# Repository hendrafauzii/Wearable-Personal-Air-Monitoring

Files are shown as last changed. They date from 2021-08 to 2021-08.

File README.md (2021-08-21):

# Wearable Personal Air Monitoring

## Daftar Isi
 - [Daftar Isi](#Daftar-isi)  
 - [Deskripsi](#Deskripsi) 
 - [Library Depedency](#Library-depedency)
 - [PCB Design](#PCB-Design) 
 - [Bill of Materials](#BOMs) 
 - [Dashboard](#dasboard-pada-platform-iot-xl-axiata-flex-iot)
 - [Galeri](#Galeri)

## Deskripsi
Perangkat ini dirancang pada tahun 2019 yang dibuat menyerupai sebuah jam tangan bagi penderita sinusitis yang sensitif terhadap perubahan udara. Terdapat beberapa sensor yang digunakan diantaranya  sensor BME280 sebagai pengukuran suhu, kelembapan, dan tekanan udara secara real time, dan MAX30105 sebagai sensor tambahan yang berfungsi untuk mengukur detak jantung. Alat ini akan memberikan notifikasi ketika kondisi udara tidak ideal bagi penderita sinusitis.

## Library Depedency
Perangkat ini diprogram menggunakan ArduinoIDE yang berbasis C/C++, dengan memilih ESP32 Dev Module pada bagian board di ArduinoIDE.
Adapun library depedency yang digunakan diantaranya :

**• Adafruit Sensor** https://github.com/adafruit/Adafruit_Sensor

**• BME280** https://downloads.arduino.cc/libraries/github.com/adafruit/Adafruit_BME280_Library-1.1.0.zip

**• MAX3010x** https://github.com/sparkfun/SparkFun_MAX3010x_Sensor_Library

**• SSD1306 Display** https://github.com/ThingPulse/esp8266-oled-ssd1306

**• PubSub Client** https://github.com/knolleary/pubsubclient

**• ArduinoJson v5** https://github.com/bblanchon/ArduinoJson/tree/5.x

## PCB Design
<p align="left"> 
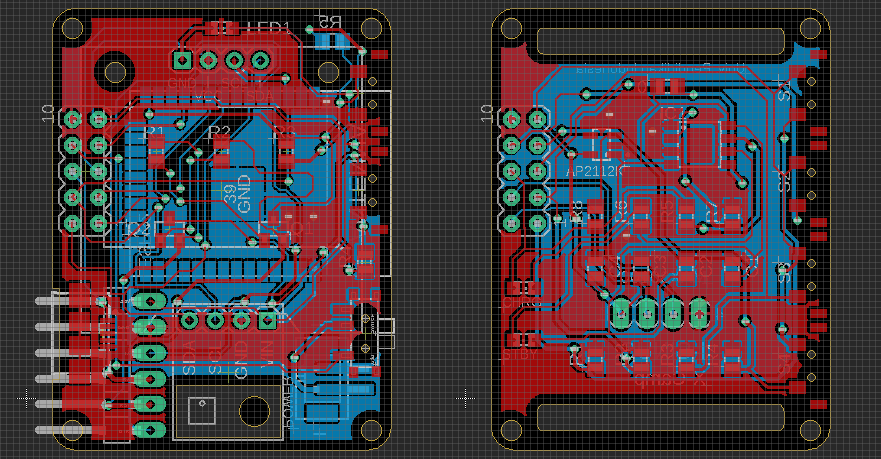
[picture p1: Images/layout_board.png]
  
</p>

## BOMs
**• Bagian Atas**
No | Parts          | Value       | Package                  | Qty 
-- | -------------- | ----------- | ------------------------ | --- |
1  | LED1           | LED         | CHIPLED_0805             |  1  |
2  | SV1	           | MA05        | MA05-2	                  |  1  |
3  | JP1            | PIN HEAD    | 1X06/90                  |  1  |
4  | U$3, U$4       | SIDE SWITCH | SIDE_SWITCH              |  2  |
5  | R1, R2, R4, R5 | 10K	        | R0805                    |  4  |
6  | R3	            | 1K	         | R0805                    |  1  |
7  | U$1	           | BME280	     | BME280                   |	 1  |
8  | OLED-DISPLAY   | OLED-128X64 | 128X64-I2C               |	 1  |
9  | U1	            | ESP32	      | ESP32-WROOM              |  1  |
10 | J1	            | MICRO USB	  | GCT_USB3065-XX-00-A_REVE |  1  |
11 | Q1, Q2	        | MMBT2222A	  | SOT23                    |  2  |
12 | X1	            | POWER       | B2B-PH-SM4-TB            |  1  |
13 | U$2	           | SWITCH	     | MSK-12C02                |  1  |

**• Bagian Bawah**
No | Parts              | Value    | Package          | Qty 
-- | ------------------ | -------- | ---------------- | --- |
1  | CHRG, STBY	        | LED      | CHIPLED_0805     |	 2  |
2  | MAX30100	          | MAX30100 |	MA04-1           |	 1  |
3  | SV1                | MA05-2   |	MA05-2           |	 1  |
4  | 0 (Not Used)       | 0        |	R0805            |	 1  |
5  | R1, R2, R3, R4, R8 | 10K      |	R0805            |	 5  |
6  | C1, C2, C3         | 10uF     |	C0805            |  3  |
7  | R5, R6             | 1K       |	R0805            |  2  |
8  | C4                 | 1uF      |	C0805            |  1  |
9  | R7                 | 2K       |	R0805            |  1  |
10 | U2                 | AP2112K  |	SOT95P285X140-5N |  1  |
11 | S1                 |	BUT1     |	SIDE_SWITCH      |  1  |
12 | S2                 |	BUT2     |	SIDE_SWITCH	     |  1  |
13 | S3                 |	BUT3     |	SIDE_SWITCH	     |  1  |
14 | S4                 |	BUT4     |	SIDE_SWITCH	     |  1  |
15 | IC1                |	TP4056   |	SOP-8	           |  1  |

## Dasboard pada Platform IoT XL Axiata (Flex-IoT)
Perangkat ini dihubungkan dengan Platform IoT XL Axiata [(Flex-IoT)](https://portal.flexiot.xl.co.id/) menggunakan WiFi dengan Protokol MQTT, sehingga dapat dibuat dashboard untuk monitoring seperti yang terlihat pada gambar berikut. 

<p align="left"> 
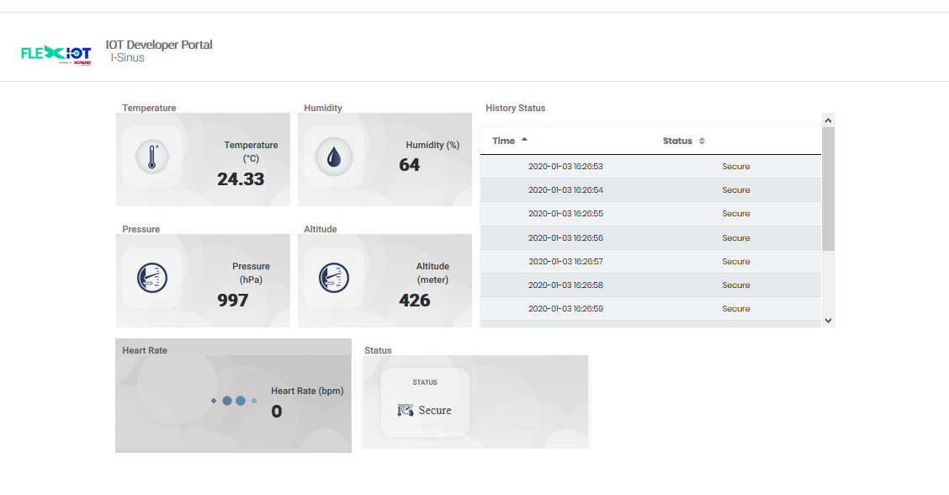
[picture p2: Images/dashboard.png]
  
</p>

## Galeri
No |  Gambar                                                                                                                     | Keterangan         
-- |  -------------------------------------------------------------------------------------------------------------------------- | ------------------------- |
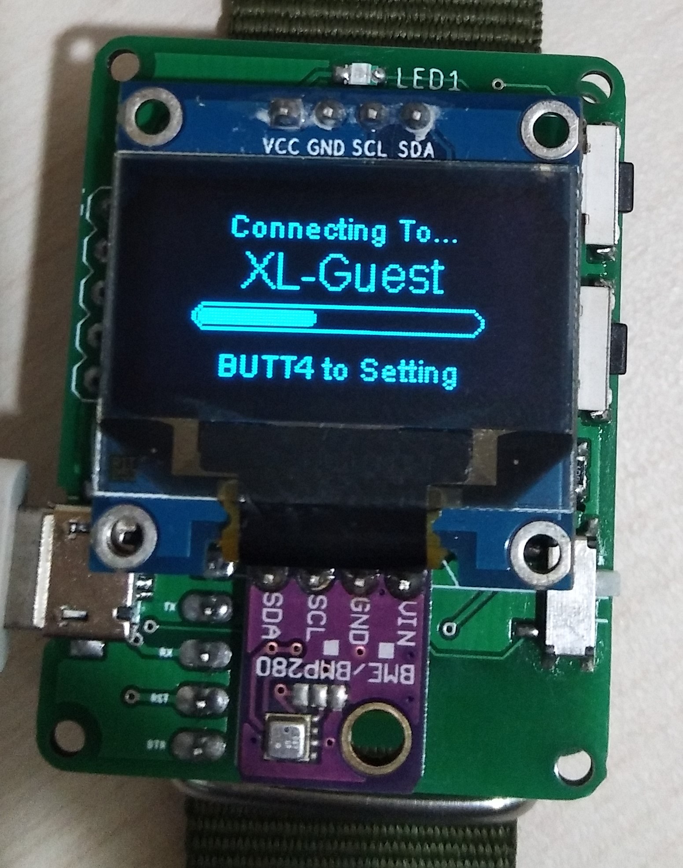
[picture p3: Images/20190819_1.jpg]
1  |   | Menghubungkan ke WiFi     |
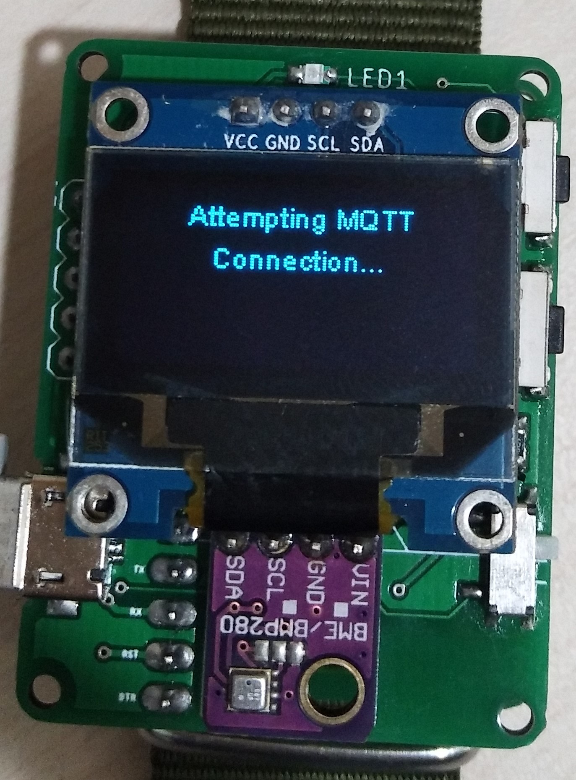
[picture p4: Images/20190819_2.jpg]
2  |   |	Menghubungkan dengan MQTT |
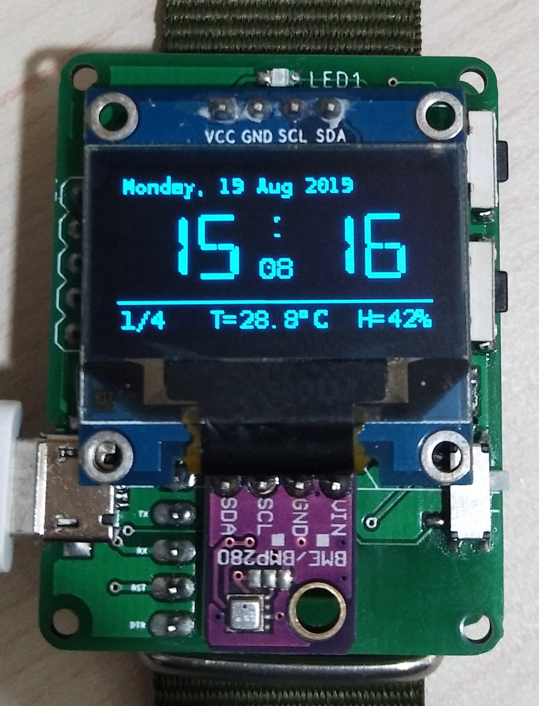
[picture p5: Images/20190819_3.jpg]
3  |   |	Tampilan utama berupa suhu lingkungan sekitar,      kelembapan udara, dan jam digital.          |
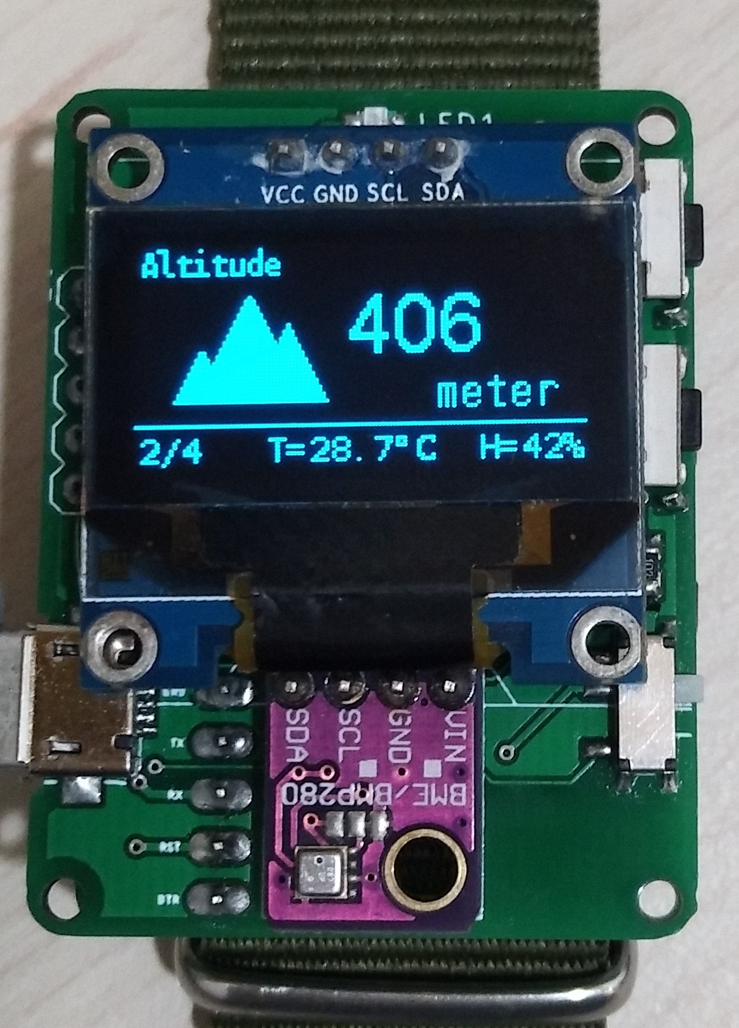
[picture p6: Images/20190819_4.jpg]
4  |   | Slide kedua merupakan ***altitude*** atau ketinggian dari permukaan bumi.     |
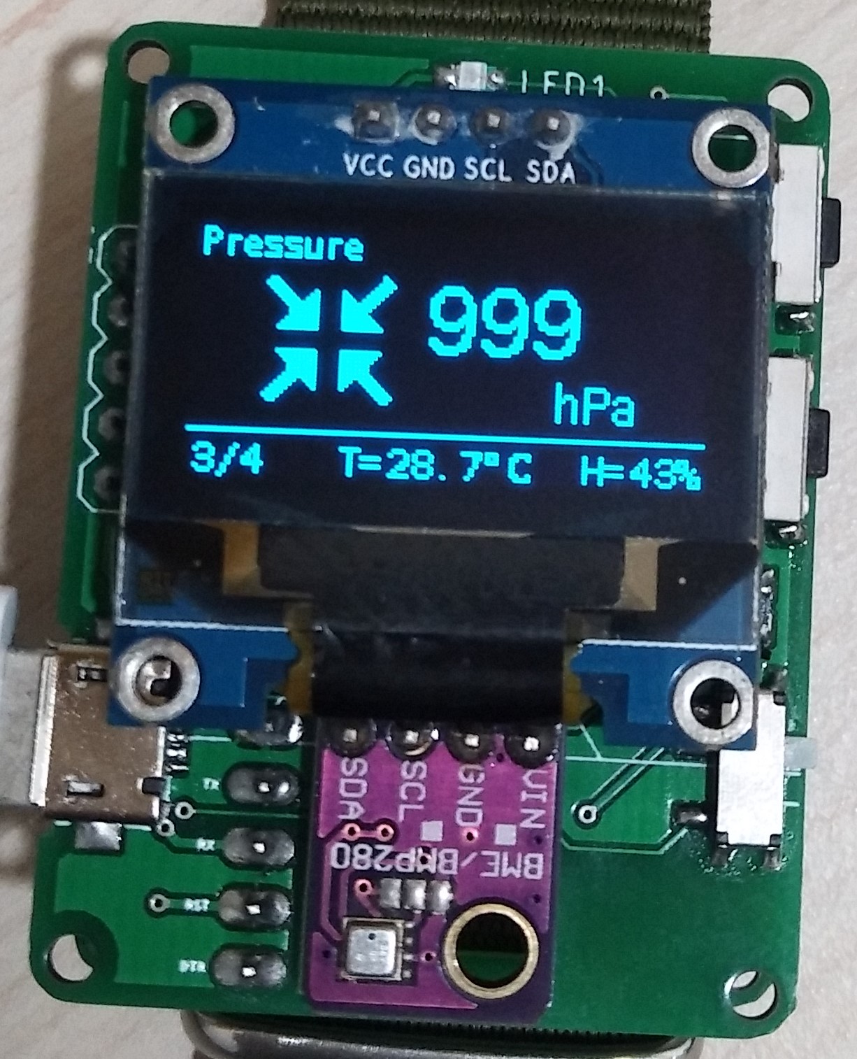
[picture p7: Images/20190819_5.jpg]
5  |   |	Slide ketiga merupakan tekanan udara sekitar. |
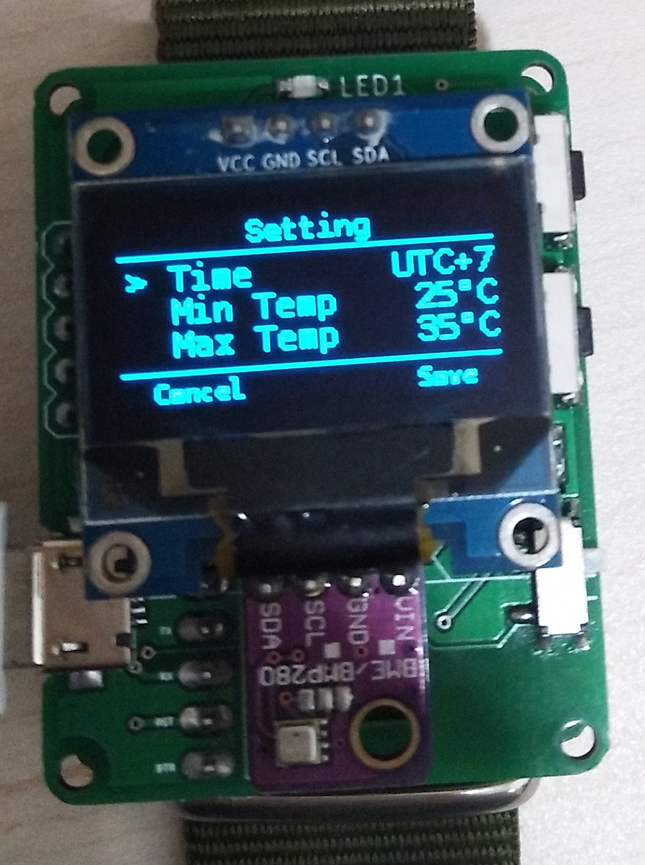
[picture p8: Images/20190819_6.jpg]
6  |   |	Pengaturan zona wktu dan batas suhu maksimal dan minimum |

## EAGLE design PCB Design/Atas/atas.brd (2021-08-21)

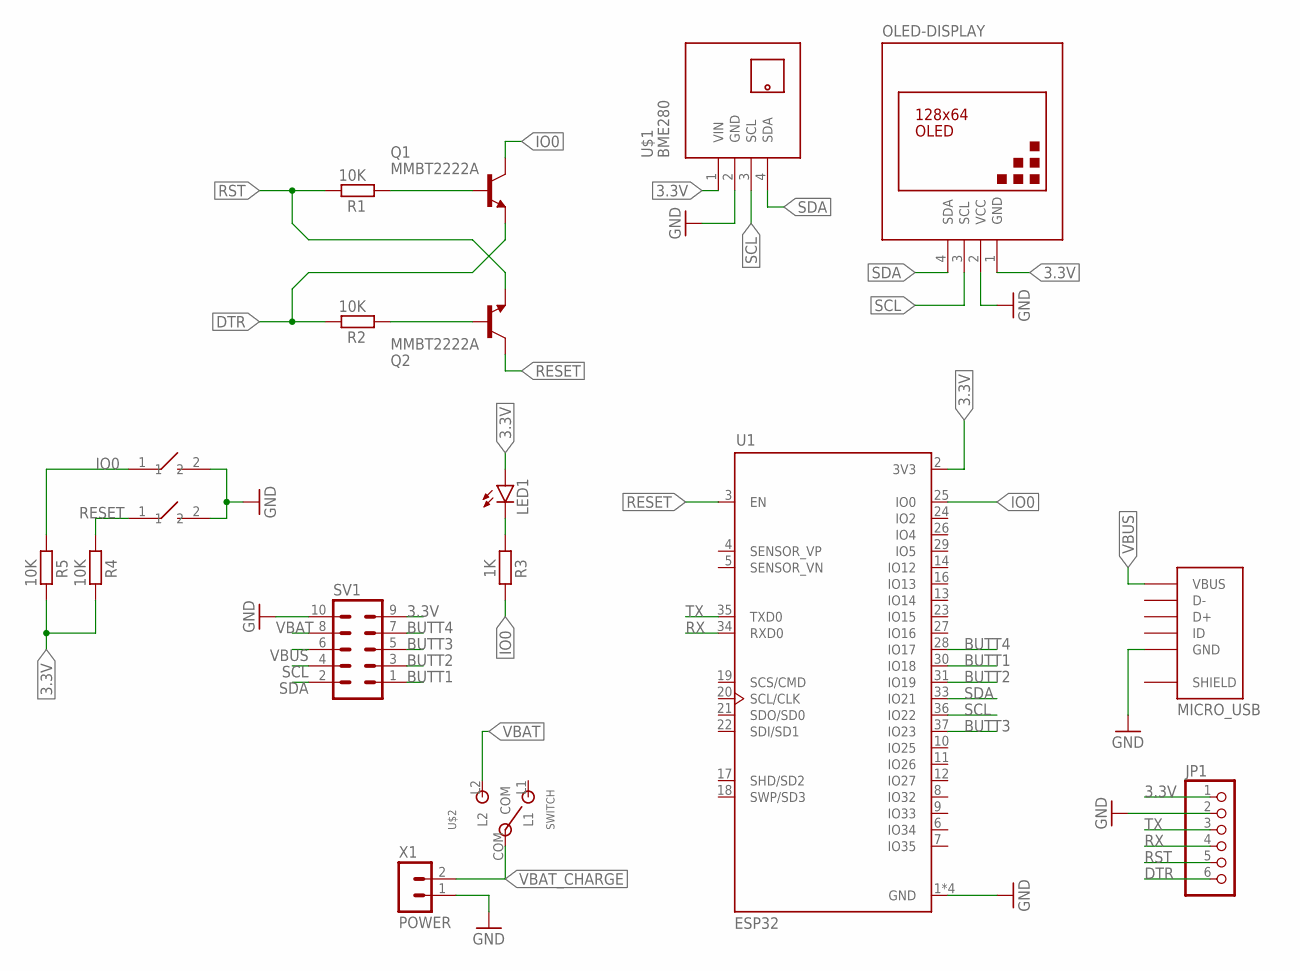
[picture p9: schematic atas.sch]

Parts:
J1: MICRO_USB; GCT_USB3065-XX-00-A_REVE
JP1: PINHD-1X6/90; 1X06/90
LED1: LEDCHIPLED_0805; CHIPLED_0805
OLED-DISPLAY: DISPLAY-OLED-128X64-I2C
Q1, Q2: MMBT2222A; SOT23
R1, R2, R4, R5: 10K; R0805
R3: 1K; R0805
SV1: MA05-2
U1: ESP32; MODULE_ESP32-WROOM-32D
U$1: BME280; TEMP-HUM-PRES-BME280
U$2: SWITCH; MSK-12C02
U$3, U$4: SIDE_SWITCH
X1: POWER; B2B-PH-SM4-TB

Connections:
3.3V: JP1.1, LED1.A, OLED-DISPLAY.1 (GND), R4.2, R5.2, SV1.9, U1.2 (3V3), U$1.1 (VIN)
BUTT1: SV1.1, U1.30 (IO18)
BUTT2: SV1.3, U1.31 (IO19)
BUTT3: SV1.5, U1.37 (IO23)
BUTT4: SV1.7, U1.28 (IO17)
DTR: JP1.6, Q1.2 (E), R2.2
GND: J1.5 (GND), JP1.2, OLED-DISPLAY.2 (VCC), SV1.10, U1.1 (GND), U1.15 (GND), U1.38 (GND), U1.39 (GND), U$1.2 (GND), U$3.2 (1), U$4.2 (1), X1.1
IO0: Q1.3 (C), R3.2, R5.1, U1.25 (IO0), U$3.1 (2)
unnamed: Q1.1 (B), R1.1
unnamed: Q2.1 (B), R2.1
unnamed: LED1.C, R3.1
RESET: Q2.3 (C), R4.1, U1.3 (EN), U$4.1 (2)
RST: JP1.5, Q2.2 (E), R1.2
RX: JP1.4, U1.34 (RXD0)
SCL: OLED-DISPLAY.3 (SCL), SV1.4, U1.36 (IO22), U$1.3 (SCL)
SDA: OLED-DISPLAY.4 (SDA), SV1.2, U1.33 (IO21), U$1.4 (SDA)
SHIELD: J1.6 (SHIELD), J1.7 (SHIELD), J1.8 (SHIELD), J1.9 (SHIELD)
TX: JP1.3, U1.35 (TXD0)
VBAT: SV1.8, U$2.L2
VBAT_CHARGE: U$2.COM, X1.2
VBUS: J1.1 (VBUS), SV1.6

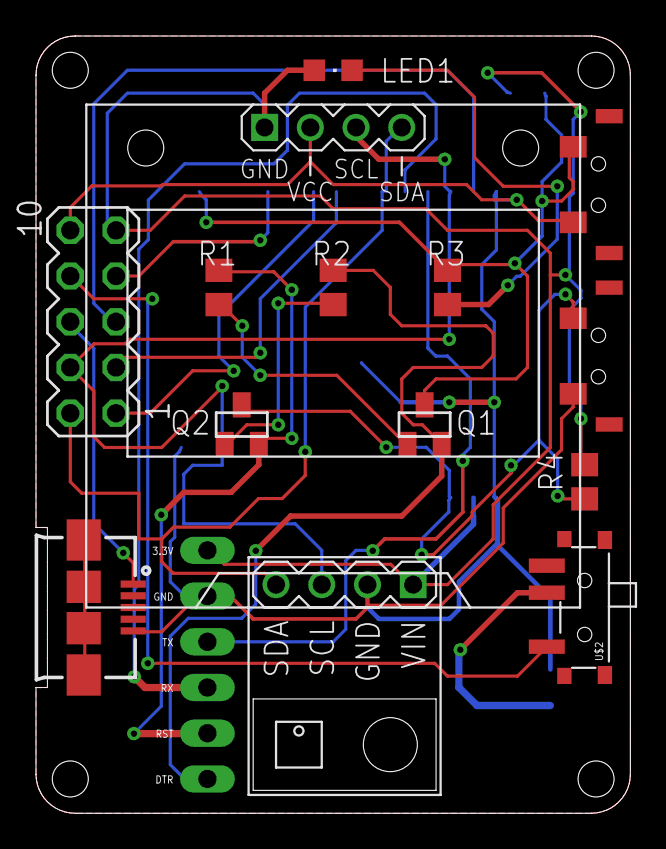
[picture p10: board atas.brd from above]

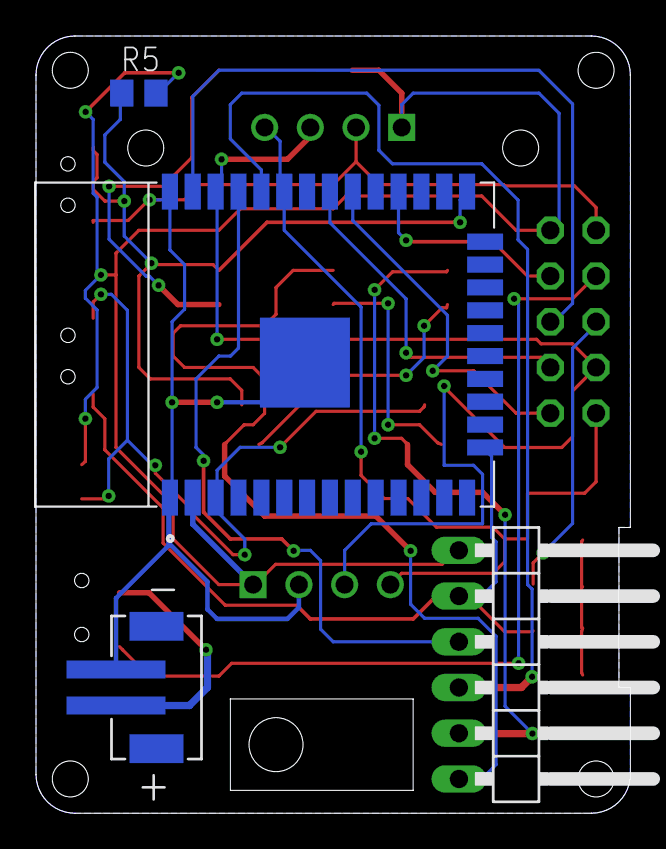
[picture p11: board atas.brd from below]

Board: 2 copper layers, 33.0 x 43.2 mm, 18 parts (4 on the bottom side), 21 nets.

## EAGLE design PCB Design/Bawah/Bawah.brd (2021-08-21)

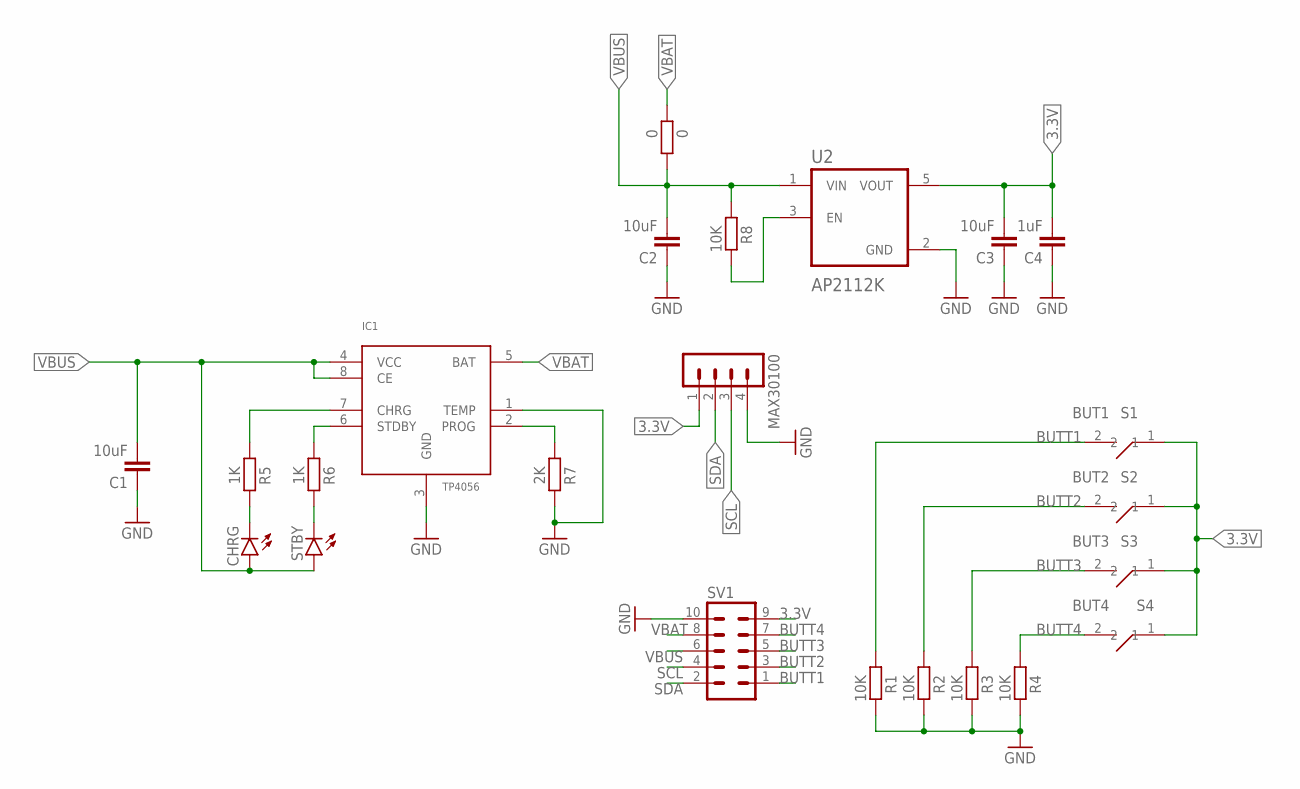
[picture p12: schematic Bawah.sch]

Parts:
0: 0; R0805
C1, C2, C3: 10uF; C0805
C4: 1uF; C0805
CHRG: LEDCHIPLED_0805; CHIPLED_0805
IC1: TP4056; SOP-8
MAX30100: MA04-1
R1, R2, R3, R4, R8: 10K; R0805
R5, R6: 1K; R0805
R7: 2K; R0805
S1: BUT1; SIDE_SWITCH
S2: BUT2; SIDE_SWITCH
S3: BUT3; SIDE_SWITCH
S4: BUT4; SIDE_SWITCH
STBY: LEDCHIPLED_0805; CHIPLED_0805
SV1: MA05-2
U2: AP2112K; SOT95P285X140-5N

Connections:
3.3V: C3.2, C4.2, MAX30100.1, S1.1 (2), S2.1 (2), S3.1 (2), S4.1 (2), SV1.9, U2.5 (VOUT)
BUTT1: R1.1, S1.2 (1), SV1.1
BUTT2: R2.1, S2.2 (1), SV1.3
BUTT3: R3.1, S3.2 (1), SV1.5
BUTT4: R4.1, S4.2 (1), SV1.7
GND: C1.1, C2.1, C3.1, C4.1, IC1.1 (TEMP), IC1.3 (GND), MAX30100.4, R1.2, R2.2, R3.2, R4.2, R7.2, SV1.10, U2.2 (GND)
unnamed: IC1.6 (STDBY), R6.1
unnamed: R8.2, U2.3 (EN)
unnamed: IC1.7 (CHRG), R5.1
unnamed: CHRG.C, R5.2
unnamed: R6.2, STBY.C
unnamed: IC1.2 (PROG), R7.1
SCL: MAX30100.3, SV1.4
SDA: MAX30100.2, SV1.2
VBAT: 0.1, IC1.5 (BAT), SV1.8
VBUS: 0.2, C1.2, C2.2, CHRG.A, IC1.4 (VCC), IC1.8 (CE), R8.1, STBY.A, SV1.6, U2.1 (VIN)

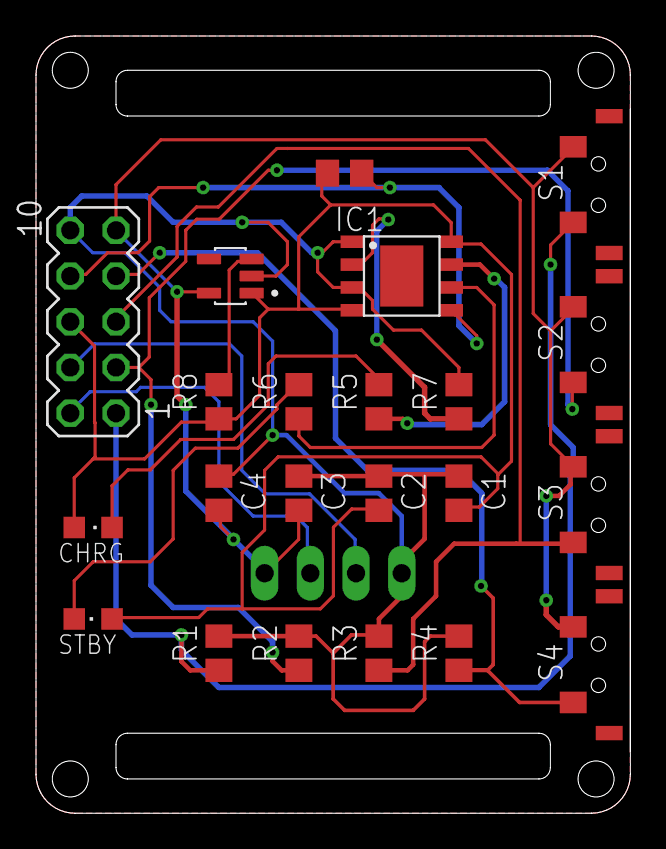
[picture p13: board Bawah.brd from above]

Board: 2 copper layers, 33.0 x 43.2 mm, 23 parts (1 on the bottom side), 16 nets.

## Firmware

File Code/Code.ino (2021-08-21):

#include <Wire.h>
#include <WiFi.h>
#include <Adafruit_Sensor.h>
#include <Adafruit_BME280.h>
#include "SSD1306Wire.h" 
#include <Arduino.h>
#include <PubSubClient.h>
#include <ArduinoJson.h>
#include "MAX30105.h"
#include "heartRate.h"
#include "EEPROM.h"
#include "time.h" 
#include "font.h"
#include "logo.h"

#define SEALEVELPRESSURE_HPA (1013.25)
#define I2C_SDA 21
#define I2C_SCL 22
#define BME280_ADD 0x76
#define OLED_ADD 0x3c
#define butt1 18
#define butt2 19
#define butt3 23
#define butt4 17

/*
 * Configure MQTT
String SUB_TOPIC_STRING = 
const char* topic_pub = 
const char* mqtt_server = 
#define mqtt_user ""
#define mqtt_password ""
*/

const char* ntpServer = "pool.ntp.org";
const int   daylightOffset_sec = 3600;
long  gmtOffset_sec;

SSD1306Wire  display(OLED_ADD, I2C_SDA, I2C_SCL);
Adafruit_BME280 bme;
MAX30105 particleSensor;
WiFiClient espClient;
PubSubClient client(espClient);

char hurufKecil[64] = {'0', '1', '2', '3', '4', '5', '6', '7', '8', '9', 'a', 'b', 'c', 'd', 
                       'e', 'f', 'g', 'h', 'i', 'j', 'k', 'l', 'm', 'n', 'o', 'p', 'q', 'r',
                       's', 't', 'u', 'v', 'w', 'x', 'y', 'z', '{', '}', '[', ']', '|', '$', 
                       '&', '*', '(', ')', '-', '_', '+', '=', '#', '&', '@', '!', ';', '^', 
                       '<', '>', ',', '.', '/', '?', '%', ':'
                      }; // 0 - 63 data

char hurufBesar[64] = {'0', '1', '2', '3', '4', '5', '6', '7', '8', '9', 'A', 'B', 'C', 'D', 
                       'E', 'F', 'G', 'H', 'I', 'J', 'K', 'L', 'M', 'N', 'O', 'P', 'Q', 'R',
                       'S', 'T', 'U', 'V', 'W', 'X', 'Y', 'Z', '{', '}', '[', ']', '|', '$', 
                       '&', '*', '(', ')', '-', '_', '+', '=', '#', '&', '@', '!', ';', '^', 
                       '<', '>', ',', '.', '/', '?', '%',':'
                      }; // 0 - 63 data

const byte RATE_SIZE = 4;
byte rates[RATE_SIZE];
byte rateSpot = 0;
long lastBeat = 0;
long irValue = 0;
int beatsPerMinute = 0;
int beatAvg;

double temp;
int pressure, altitude, humidity;
char tempHum[32];

unsigned long startMillis;
unsigned long start1Millis;
unsigned long currentMillis;
const unsigned long interval = 1000;

char dayDate[32];
char hourNow[3];
char minuteNow[3];
char secondNow[3];

char ssid[32];
char password[32];
char bufferPass[32];
char saveSSID[32];
char savePASSWORD[32];
char jumlah_network[32];
int numSSID;

char msg[300];
                      
struct tm timeinfo;
int counter;
int progress;

int menu, menuSetting, kondisi;
bool state1, state2, state3, state4;
int waktu;
int x,y,d,e;
int a,c;
int pathIndex;
int pilihanHuruf;
int slide;

int setMinTemp;
int setMaxTemp;
int settTime;
int setAltitude;

int addSSID = 0;
int addPass = 32;
int addTime = 64;
int addMinTemp = 74;
int addMaxTemp = 84;
int addAltitude = 94;

void setup() {
  // put your setup code here, to run once:
  Serial.begin(115200);
  EEPROM.begin(128);
  display.init();
  display.flipScreenVertically();
  bme.begin(BME280_ADD);
  particleSensor.begin(Wire, I2C_SPEED_FAST);
  particleSensor.setup(); 
  particleSensor.setPulseAmplitudeRed(0x0A); 
  particleSensor.setPulseAmplitudeGreen(0);
  
  for(int i=1; i<=64; i++){
    display.clear();
    display.drawXbm(0, 0, 128, i, isinus_image); 
    display.display();
    delay(10);
  }
  delay(1000);

  for(int i=0; i<=64; i++){
    display.clear();
    display.drawXbm(0, i, 128, 64, isinus_image); 
    display.drawXbm(0, 0, 128, i, xcamp_image); 
    display.display();
    delay(5);
  }
  delay(1000);

  for(int i=0; i<=64; i++){
    display.clear();
    display.drawXbm(0-(i*4), 0, 128, 64, xcamp_image); 
    display.drawXbm(0, 0, 128, i, upi_image); 
    display.display();
    delay(5);
  }
  delay(1000);

  for(int i=1; i<=64; i++){
    display.clear();
    display.drawXbm(0-(i*2), 0, 128, 64, upi_image); 
    display.display();
    delay(5);
  }

  setup_wifi();
  configTime((EEPROM.readInt(addTime) * 60 * 60) - 3600, daylightOffset_sec, ntpServer);
  client.setServer(mqtt_server, 1883);
  client.setCallback(callback);
  
  pinMode(butt1, INPUT);
  pinMode(butt2, INPUT);
  pinMode(butt3, INPUT);
  pinMode(butt4, INPUT);
  delay(100);
  
  startMillis = millis();
}

void loop() {
  // put your main code here, to run repeatedly:
  c:
  pilihan(0, 3);
  client.loop();
  if(WiFi.status() != WL_CONNECTED) setup_wifi();   
  if(WiFi.status() == WL_CONNECTED && !client.connected()) reconnect();
  
  BMP280_read();
  currentMillis = millis();
  if(currentMillis - startMillis >= interval){ 
    startMillis = currentMillis;
    sendData_iot("Secure");
  }
  
  getLocalTime(&timeinfo);
  snprintf(tempHum, sizeof(tempHum), "T=%.1f°C  H=%02d%s", temp, humidity, "%");

  if((temp <= EEPROM.readInt(addMinTemp) || temp >= EEPROM.readInt(addMaxTemp)) && state4 == false){
    char warningTime[32];
    char tempAndTime[32];
    double warningTemp = bme.readTemperature();
    strftime(warningTime, sizeof(warningTime), "%H:%M", &timeinfo);
    snprintf(tempAndTime, sizeof(tempAndTime), "%.1f°C in %s", temp, warningTime);
    waktu=0;
    while(1){
      if(millis() - start1Millis >= 500){ 
        start1Millis = millis();
        sendData_iot("Danger");
      }           
      waktu++;
      Serial.println(waktu);
      display.clear();
      display.setTextAlignment(TEXT_ALIGN_CENTER);
      display.setFont(DejaVu_Sans_Mono_16);
      display.drawString(64, 1, "Warning!!");
      display.setFont(DejaVu_Sans_Mono_9);
      display.drawString(64, 20, "The temperature reaches");
      display.setFont(DejaVu_Sans_Mono_11);
      display.drawString(64, 33, String(tempAndTime));
      display.setTextAlignment(TEXT_ALIGN_RIGHT);
      display.setFont(DejaVu_Sans_Mono_9);
      display.drawString(120, 50, "BUTT4 to Close");
      display.display();  
      delay(1);  
      if(digitalRead(butt4) == 1 || waktu >= 8000){
        while(digitalRead(butt4) == 1);
        break;      
      }
    }
    delay(100);
    state4 = true;
  }
  
  if(temp > EEPROM.readInt(addMinTemp) && temp < EEPROM.readInt(addMaxTemp)) state4 = false;
  
  switch(menu){
    case 0  : if(!getLocalTime(&timeinfo)){
                display.clear();
                display.setTextAlignment(TEXT_ALIGN_CENTER);
                display.setFont(DejaVu_Sans_Mono_16);
                display.drawString(64, 1, "Failled get");
                display.drawString(64, 20, "Time");
                display.setFont(DejaVu_Sans_Mono_9);
                display.drawString(64, 45, "Please reset your device");
                display.display();
              }

              else{
                strftime(dayDate, sizeof(dayDate), "%A, %d %b %Y", &timeinfo);
                strftime(hourNow, sizeof(hourNow), "%H", &timeinfo);
                strftime(minuteNow, sizeof(minuteNow), "%M", &timeinfo);
                strftime(secondNow, sizeof(secondNow), "%S", &timeinfo);
   
                display.clear();
                display.drawRect(0, 52, 128, 1);
                display.setTextAlignment(TEXT_ALIGN_LEFT);
                display.setFont(DejaVu_Sans_Mono_8);
                display.drawString(1, 0, String(dayDate));
                display.setFont(DejaVu_Sans_Mono_10);
                display.drawString(1, 53, "1/4");
                display.setTextAlignment(TEXT_ALIGN_RIGHT);
                display.setFont(DejaVu_Sans_Mono_10);
                display.drawString(127, 53, String(tempHum));
                display.setTextAlignment(TEXT_ALIGN_CENTER);
                display.setFont(DSEG14_Classic_Bold_16);
                display.drawString(64, 12, ":");
                display.setFont(DejaVu_Sans_Mono_11);
                display.drawString(64, 32, String(secondNow));
                display.setFont(DSEG14_Classic_Regular_26);
                display.drawString(30, 14, String(hourNow));
                display.drawString(98, 14, String(minuteNow));
                display.display();
              } 
    break;

    case 1  : display.clear();
              display.drawRect(0, 52, 128, 1);
              display.setTextAlignment(TEXT_ALIGN_LEFT);
              display.setFont(DejaVu_Sans_Mono_9);
              display.drawString(1, 0, "Altitude");
              display.setFont(DejaVu_Sans_Mono_10);
              display.drawString(1, 53, "2/4");
              display.setTextAlignment(TEXT_ALIGN_RIGHT);
              display.setFont(DejaVu_Sans_Mono_10);
              display.drawString(127, 53, String(tempHum));

              display.drawXbm(10, 7, 46, 46, altitude_image);
              display.setTextAlignment(TEXT_ALIGN_LEFT);
              display.setFont(ArialMT_Plain_24);
              display.drawString(60, 10, String(altitude));
              display.setFont(DejaVu_Sans_Mono_12);
              display.drawString(85, 36, "meter");
              display.display();
              
              display.display();
    break;

    case 2  : display.clear();
              display.drawRect(0, 52, 128, 1);
              display.setTextAlignment(TEXT_ALIGN_LEFT);
              display.setFont(DejaVu_Sans_Mono_9);
              display.drawString(1, 0, "Pressure");
              display.setFont(DejaVu_Sans_Mono_10);
              display.drawString(1, 53, "3/4");
              display.setTextAlignment(TEXT_ALIGN_RIGHT);
              display.setFont(DejaVu_Sans_Mono_10);
              display.drawString(127, 53, String(tempHum));

              display.drawXbm(15, 11, 37, 37, pressure_image);
              display.setTextAlignment(TEXT_ALIGN_LEFT);
              display.setFont(ArialMT_Plain_24);
              display.drawString(58, 10, String(pressure));
              display.setFont(DejaVu_Sans_Mono_12);
              display.drawString(90, 36, "hPa");
              display.display();
    break;

    case 3  : read_heart();
              display.clear();
              display.drawRect(0, 52, 128, 1);
              display.setTextAlignment(TEXT_ALIGN_LEFT);
              display.setFont(DejaVu_Sans_Mono_9);
              display.drawString(1, 0, "Heart Rate");
              display.setFont(DejaVu_Sans_Mono_10);
              display.drawString(1, 53, "4/4");
              display.setTextAlignment(TEXT_ALIGN_RIGHT);
              display.setFont(DejaVu_Sans_Mono_10);
              display.drawString(127, 53, String(tempHum));

              if(irValue < 50000){
               beatsPerMinute = 0;
               display.setTextAlignment(TEXT_ALIGN_CENTER);
               display.setFont(DejaVu_Sans_Mono_12);
               display.drawString(64, 23, "Not Detection");
              }

              else{ 
               display.setTextAlignment(TEXT_ALIGN_LEFT);
               display.setFont(ArialMT_Plain_24);
               display.drawString(75, 10, String(beatsPerMinute));
               display.drawXbm(0, 0, 128, 64, heart_image);
              }  
              display.display();
    break;
  }

  if(digitalRead(butt4) == 1){
    while(digitalRead(butt4) == 1);
    char TimeSet[32];
    char minTempSett[32];
    char maxTempSett[32]; 
    settTime = EEPROM.readInt(addTime);
    setMinTemp = EEPROM.readInt(addMinTemp);
    setMaxTemp = EEPROM.readInt(addMaxTemp);
    setAltitude = EEPROM.readInt(addAltitude); 
    menuSetting = 0;
    slide = 0;
    
    while(1){
      snprintf(minTempSett, sizeof(minTempSett), "%d°C", setMinTemp);
      snprintf(maxTempSett, sizeof(maxTempSett), "%d°C", setMaxTemp);
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

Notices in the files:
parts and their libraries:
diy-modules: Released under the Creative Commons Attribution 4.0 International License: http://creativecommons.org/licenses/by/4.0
